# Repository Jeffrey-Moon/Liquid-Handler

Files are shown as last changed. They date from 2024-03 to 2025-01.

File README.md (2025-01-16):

# Construction of a Low-cost Liquid Handling Device with 3D Printing for Polymerase Chain Reaction V1

This repository contains the source code and instructions for constructing a low-cost automated liquid handling device designed specifically for performing Polymerase Chain Reaction (PCR) tasks. This device is ideal for underfunded laboratories looking for an affordable solution to automate repetitive pipetting tasks. For a clear and concise summary about the project, please read the [Construction of a Low-cost Liquid Handling Device with 3D Printing for Polymerase Chain Reaction.pdf](assets/Construction_of_a_Low-cost_Liquid_Handling_Device_with_3D_Printing_for_Polymerase_Chain_Reaction.pdf)

## Abstract

Although a field still in its infancy, robots, and automated devices have been adopted in an increasing number of laboratories to make the workflow more efficient. However, the high cost of liquid handling devices exacerbates disparities between laboratories. To address this issue, this research developed an accurate and low-cost liquid handler, designed for easy replication through open-source software and 3D designs distributed online. The device was rigorously tested, achieving a systematic error of 2.54% at 5 µL and a random error of 1.82%, yielding an overall accuracy of 97.46% and precision of 98.18%. Polymerase Chain Reaction (PCR) tests and gel electrophoresis analysis confirmed the machine’s capability to accurately perform PCR. With a material cost of approximately $206, this device offers a highly economical alternative to commercial liquid handlers, which typically range from $9,000 to $60,000. This innovation has the potential to significantly benefit underfunded laboratories, providing a cost-effective solution for repetitive PCR processes.

## Construction

The bill of materials and the details about the 3D print components are in the pdf [Liquid_Handler_Materials.pdf](assets/Liquid_Handler_Materials.pdf) (The bill of materials were last updated on Aug 19th, 2024 and the prices might have altered over time). Download the PDF to access the links used to buy each component. The required 3D print files are located in the stl folder.

## Running the Device

1. Clone the directory into the directory you desire by `git clone https://github.com/Jeffrey-Moon/Liquid-Handler.git`
1. Upload the Arduino code Liquid_Handler.ino after connecting the computer to the Arduino using the cable.
1. Plug in the device and turn the device on.
1. Download python if not already and download the required library by either running `pip install pyserial` or `pip install -r requirements.txt`.
1. Run the python code after creating your own sequence.

Example:
`python code/pyserial_control.py  --repetitions 1 2 3 --from_coords 0,0 1,1 2,2 --to_coords 3,3 4,4 5,5 --tube_types B T B`
This would execute a sequence of operations: First, attach a tip, then transfer from big tube (0,0) to small tube (3,3) once. Next, change the tip, then transfer from small tube (1,1) to small tube (4,4) twice. Finally, change the tip, then transfer from big tube (2,2) to small tube (5,5) three times.
--repetitions indicate the number of times the sequence will be executed. --from_coords is the coordinate that the device will pipette from and the --to_coords is the coordinate the device will pipette to. Lastly the --tube_types indicate the tube type for the pipetting. B indicates pipetting from the big tubes to the small tubes and T indicates pipetting from the small tubes to small tubes. The coordinate visualization for the tube racks are as seen below.

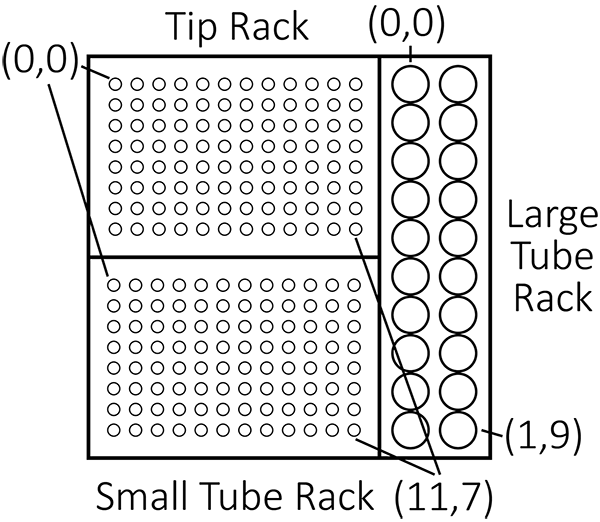
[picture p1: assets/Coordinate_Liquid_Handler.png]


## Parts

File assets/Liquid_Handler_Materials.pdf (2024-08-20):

Name | Price ($) | Amount | Total Price ($)
4 pcs 2020 V Type Aluminum Profile
300mm (https://www.amazon.com/dp/B0BZQCCP4P?ref=ppx_yo2ov_dt_b_product_details&th=1) | $ 15.99 | 3 | $ | 47.97
20 Sets Black 202 Series Aluminum
Profile Connector Set, 20 Pcs Comer
Bracker, 20Pcs T Nuts and Hex Screw
Bolt (https://www.amazon.com/dp/B0855V2JV3?ref=ppx_yo2ov_dt_b_product_details&th=1) | $ 19.97 | 1 | $ | 19.97
2 Pcs 5mm to 8mm Aluminum
Flexible Shaft Coupling D20 L25 (https://www.amazon.com/Zeberoxyz-Aluminium-Diameter20mm-Length25mm-Motor%EF%BC%885x8mm%EF%BC%89/dp/B08QV7SVH7?sp_csd=d2lkZ2V0TmFtZT1zcF9hdGY) | $ 11.99 | 1 | $ | 11.99
2 Pcs 8mm x 300mm Case Hardened
Chrome Plated Linear Motion Rod
Shaft Guide (https://www.amazon.com/dp/B07DPF612G?psc=1&ref=ppx_yo2ov_dt_b_product_details) | $ 9.99 | 2 | $ | 19.98

10 Pcs GT2 Pulley Wheel 20 Teeth
5mm Bore Aluminum Timing Belt Idler
Pulley for 3D Printer 6mm Width (https://www.amazon.com/3Dman-Pulley-Timing-Aluminum-Printer/dp/B085XLRXS1) | $ 8.99 | 1 | $ | 8.99
2 Pcs 8mm x 150mm Linear Motion
Rod Shaft Guide (https://www.amazon.com/dp/B08HYJTR54?psc=1&ref=ppx_yo2ov_dt_b_product_details) | $ 8.99 | 1 | $ | 8.99
GT2 Timing Belt 10 Meters Length
2mm Pitch 6mm Width Rubber Drive
Belt (https://www.amazon.com/dp/B097T3Y6WW?psc=1&ref=ppx_yo2ov_dt_b_product_details) | $ 9.99 | 1 | $ | 9.99
150mm Length T8 8mm Diameter
Lead Screw Rod with Copper Nut
Trapezoidal Thread for 3D Printer Z
Axis2pcs (https://www.amazon.com/dp/B07QV57SYP?psc=1&ref=ppx_yo2ov_dt_b_product_details) | $ 11.89 | 1 | $ | 11.89
1.5m 220V AC Cord (Only for 220V
countries) | $ 1.34 | 1 | $ | 1.34

Inc PS615143 3-Wire Appliance and
Power Tool Cord, 6 ft, 14 AWG,
15A/125V AC, 1875w , Black (https://www.amazon.com/dp/B07BQ8MRKR?psc=1&ref=ppx_yo2ov_dt_b_product_details) | $ 5.40 | 1 | $ | 5.40

3Pcs Nema 17 Stepper Motor
42BYGH 1.8 Degree 1.5A 42 Motor
(17HS4401S) 42N.cm (60oz.in) 4-
Lead with 1m Cable and Connector
for DIY CNC 3D Printer (Pack of 3) (https://www.amazon.com/dp/B07KW6B3ZX?psc=1&ref=ppx_yo2ov_dt_b_product_details) | $ 23.99 | 1 | $ | 23.99
6Pcs Round Rocker Switch AC 6A
125V 10A 250V SPST 3 Pins 2 Position
ON/Off Red and Green LED Light
Illuminated Round Boat Rocker
Switch Toggle (https://www.amazon.com/dp/B07QG1W93X?psc=1&ref=ppx_yo2ov_dt_b_product_details) | $ 7.99 | 1 | $ | 7.99

The prices were last updated on August 19th, 2024 and it may change over time

3D Printer CNC Shield V3 Engraver
Expansion Board with 4X A4988 Driver
Module and 4 x Radiator (https://www.amazon.com/dp/B07TT3C3HB?psc=1&ref=ppx_yo2ov_dt_b_product_details) | $ 10.99 | 1 | $ | 10.99
Arduino UNO R3 Board ATmega328P
w Cable (https://www.amazon.com/ATmega328P-Arduino-Compatible-Arduino-Voltage-Compatible/dp/B0D83J2TJJ) | $ 7.99 | 1 | $ | 7.99

DC 12V 10A 120W Power Supply
SMPS Adapter Transformer Switch AC
110V/220V to DC 12V 10A (https://www.amazon.com/dp/B078RTV9C4?psc=1&ref=ppx_yo2ov_dt_b_product_details) | $ 17.99 | 1 | $ | 17.99
Servo Tower Pro MG92B Digital Metal
Gear (https://www.aliexpress.us/item/3256805501735626.html?src=google&gatewayAdapt=glo2usa) | $ 8.53 | 1 | $ | 8.53
1kg PLA Filament (https://www.amazon.com/ELEGOO-Filament-Dimensional-Accuracy-Cardboard/dp/B0BM739JRF) | $ 13.99 | 2 | $ | 27.98

2020 V Type Aluminum Profile
300mm | $ (3.99) | 2 | $ | (7.98)
5mm to 8mm Aluminum Flexible
Shaft Coupling D20 L25 | $ (7.57) | 1 | $ | (7.57)

ST2 Pulley Wheel 20 Teeth 5mm
Bore Aluminum Timing Belt Idler
Pulley for 3D Printer 6mm Width | $ (1.24) | 8 | $ | (9.92)
Round Rocker Switch AC 6A 125V
10A 250V SPST 3 Pins 2 Position
ON/Off Red and Green LED Light
Illuminated Round Boat Rocker
Switch Toggle | $ (1.33) | 5 | $ | (6.65)
150mm Length T8 8mm Diameter
Lead Screw Rod with Copper Nut
Trapezoidal Thread for 3D Printer Z
Axis | $ (6.25) | 1 | $ | (6.25)
0.5 kg PLA filament | $ (7.62) | 1 | $ | (7.62)
SUM | $ | 205.99

EXCESS

Component Name Amount

Fillament
Weight (g)

Density
(%)

Total Weight
(g)
Working Area | 1 | 295.9 | 10 | 295.9
Pipette Tip Ejecctor | 1 | 0.5 | 10 | 0.5
Pipette Clamp | 1 | 88.7 | 75 | 88.7
Base Part | 4 | 119.4 | 50 | 477.6
Base Holder | 4 | 3.4 | 100 | 13.6
8mm Bore Linear Motion Guide
Helper | 4 | 2 | 100 | 8
8mm Bearing | 6 | 0.4 | 100 | 2.4

18mm Wide 6mm Belt 8mm
Bore Pulley Wheel Type 1 | 4 | 2 | 100 | 8

18mm Wide 6mm Belt 8mm
Bore Pulley Wheel Type 2 | 2 | 2.1 | 100 | 4.2
XY Axis Linear Guide Holder
Type 1 Left | 1 | 30.1 | 100 | 30.1
XY Axis Linear Guide Holder
Type 1 Right | 1 | 30.1 | 100 | 30.1
XY Axis Linear Guide Holder
Type 2 Left | 1 | 32.7 | 100 | 32.7
XY Axis Linear Guide Holder
Type 2 Right | 1 | 32.7 | 100 | 32.7
XY Axis Linear Motion Guide | 2 | 95.5 | 100 | 191
XY Axis Motor Holder Left | 1 | 75.7 | 100 | 75.7
XY Axis Motor Holder Right | 1 | 75.7 | 100 | 75.7
Z Axis Movement Bottom | 1 | 42.2 | 50 | 42.2
Z Axis Stepper Motor Body | 1 | 62.6 | 50 | 62.6
Z Axis Stepper Motor Top | 1 | 11.4 | 25 | 11.4
Large Tube Rack | 1 | 218 | 25 | 218
Servo Extension | 1 | 0.5 | 20 | 0.5
SUM | 1701.6

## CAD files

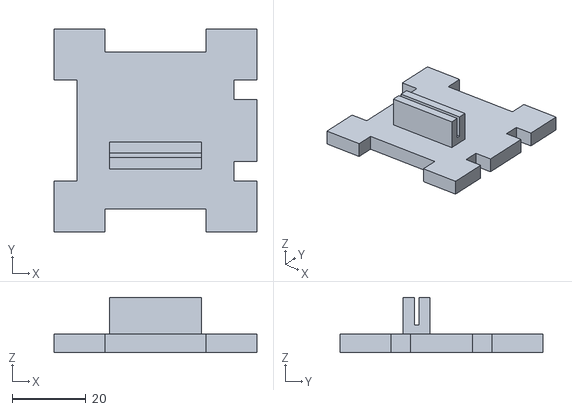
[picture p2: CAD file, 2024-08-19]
stl/Z Axis Stepper Motor Top.stl
55.0 x 55.0 x 15.0

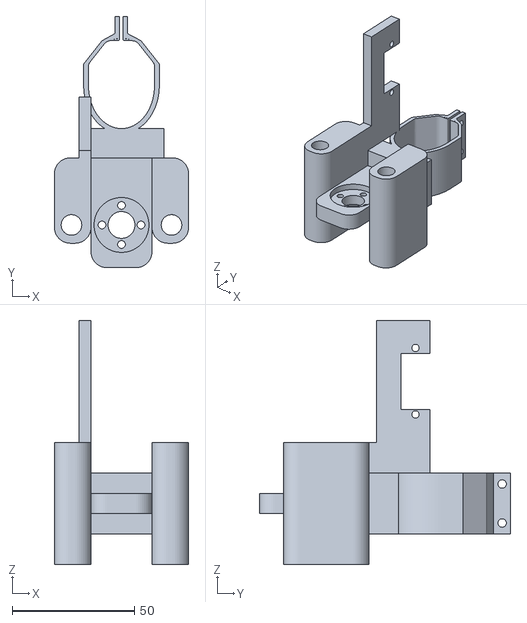
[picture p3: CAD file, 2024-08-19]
stl/Pipette Clamp.stl
55.0 x 103.0 x 100.0

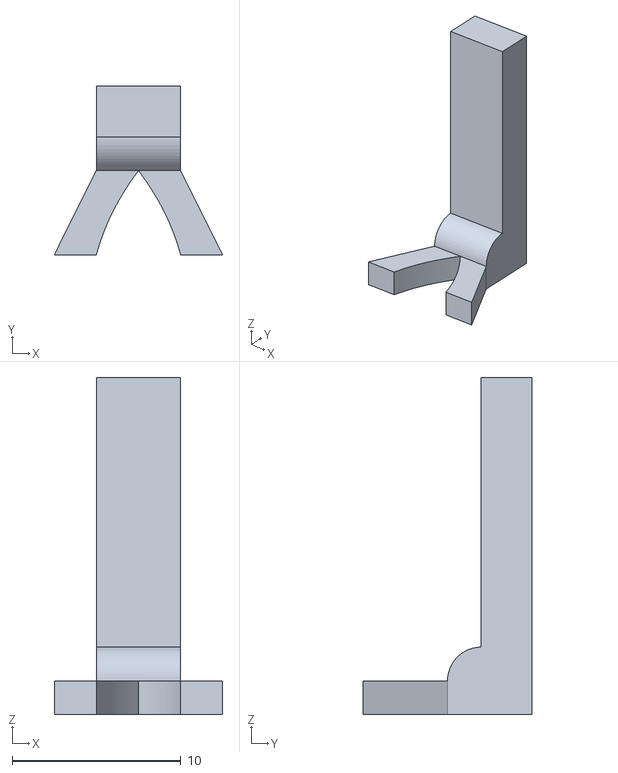
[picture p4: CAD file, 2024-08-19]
stl/Pipette Tip Ejector.stl
10.00 x 10.0 x 20.0

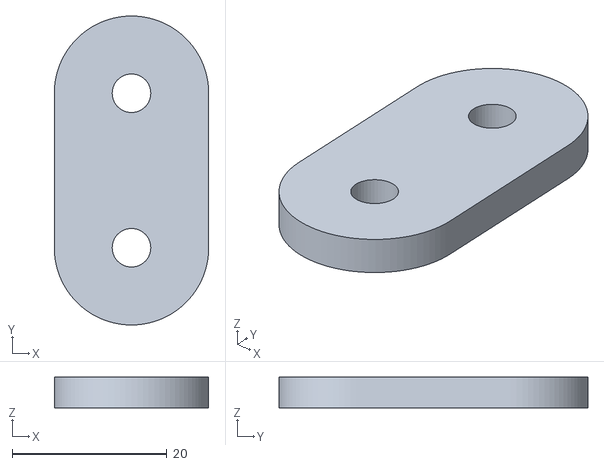
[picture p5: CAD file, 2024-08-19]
stl/Base Holder.stl
20.0 x 40.0 x 4.00

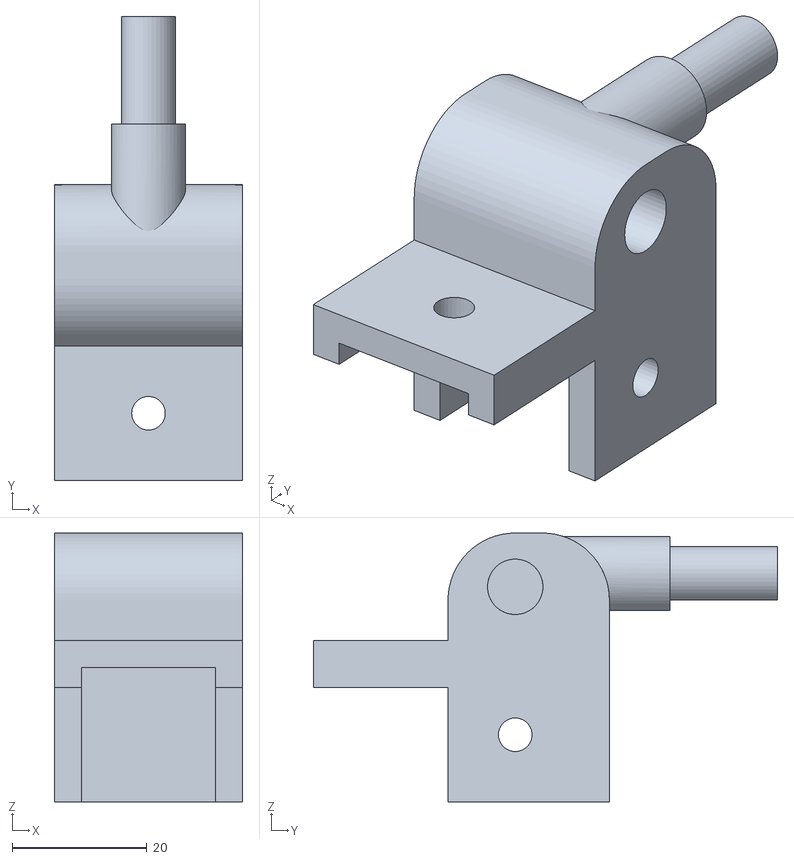
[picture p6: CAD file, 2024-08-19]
stl/XY Axis Linear Guide Holder Left.stl
28.0 x 69.0 x 40.0

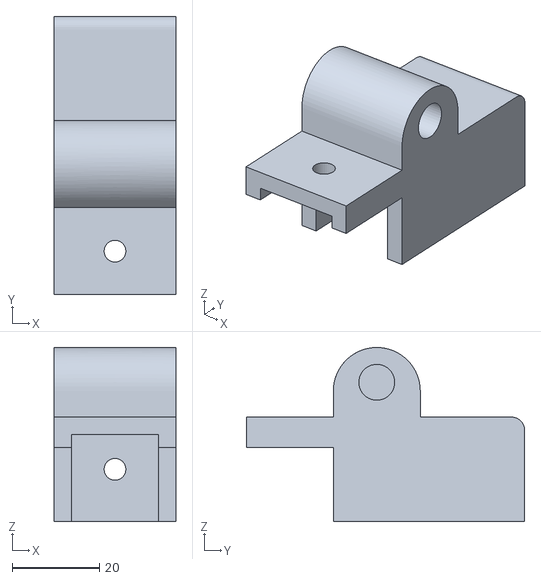
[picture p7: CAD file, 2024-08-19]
stl/XY Axis Linear Guide Holder 2 Right.stl
28.0 x 64.0 x 40.0

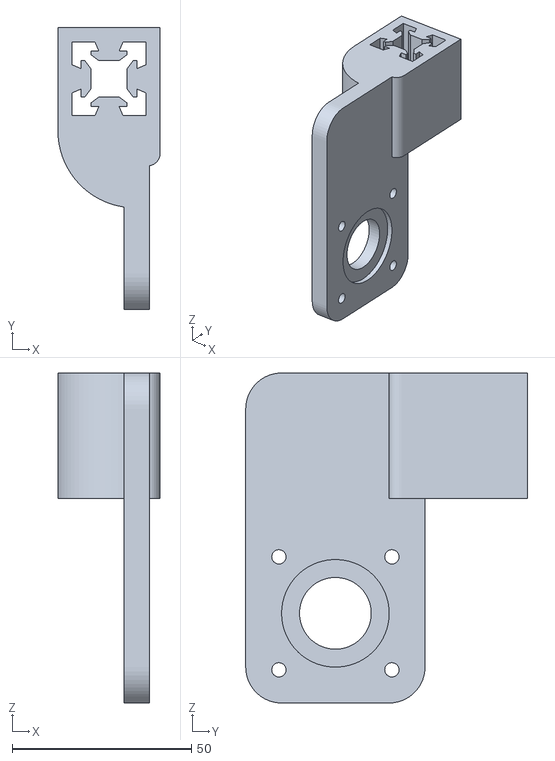
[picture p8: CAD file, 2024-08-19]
stl/XY Axis Motor Holder Left.stl
28.5 x 78.5 x 92.0

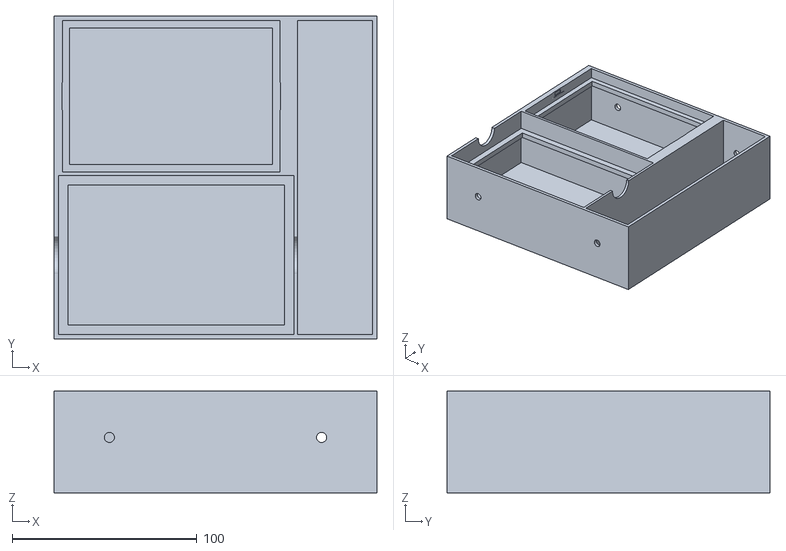
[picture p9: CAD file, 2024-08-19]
stl/Working Area.stl
175.0 x 175.0 x 55.0

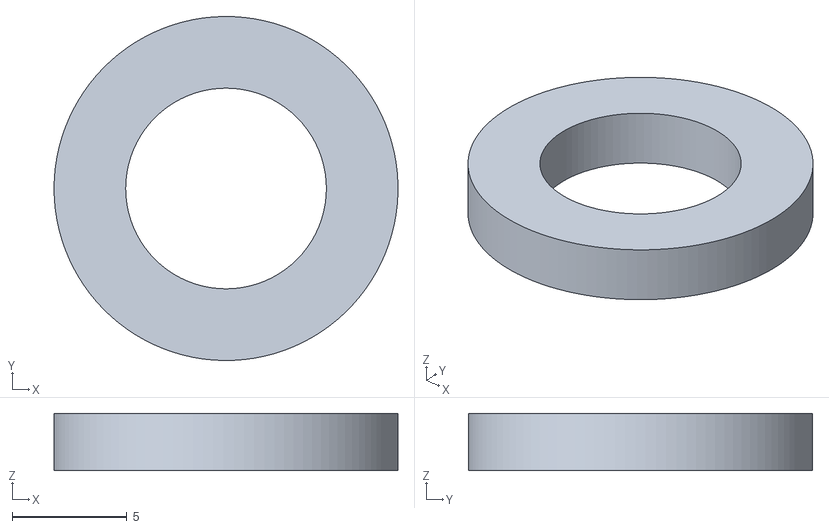
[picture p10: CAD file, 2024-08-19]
stl/8mm Bearing.stl
15.0 x 15.0 x 2.50

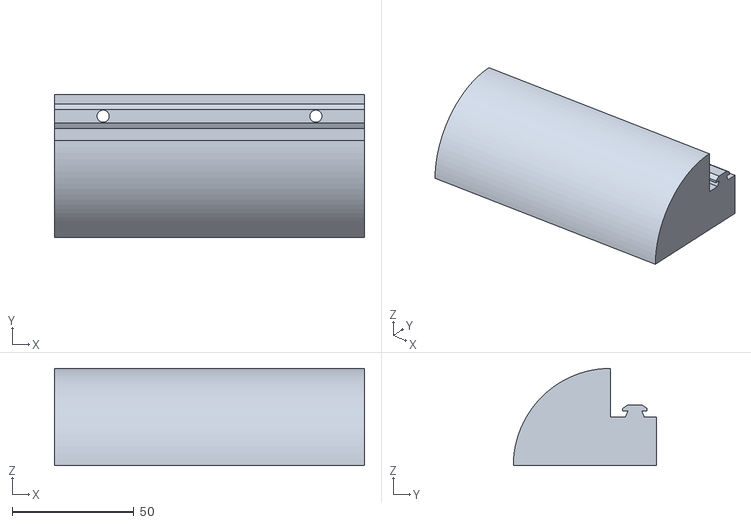
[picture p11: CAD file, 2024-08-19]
stl/Base Part.stl
127.5 x 59.0 x 40.0

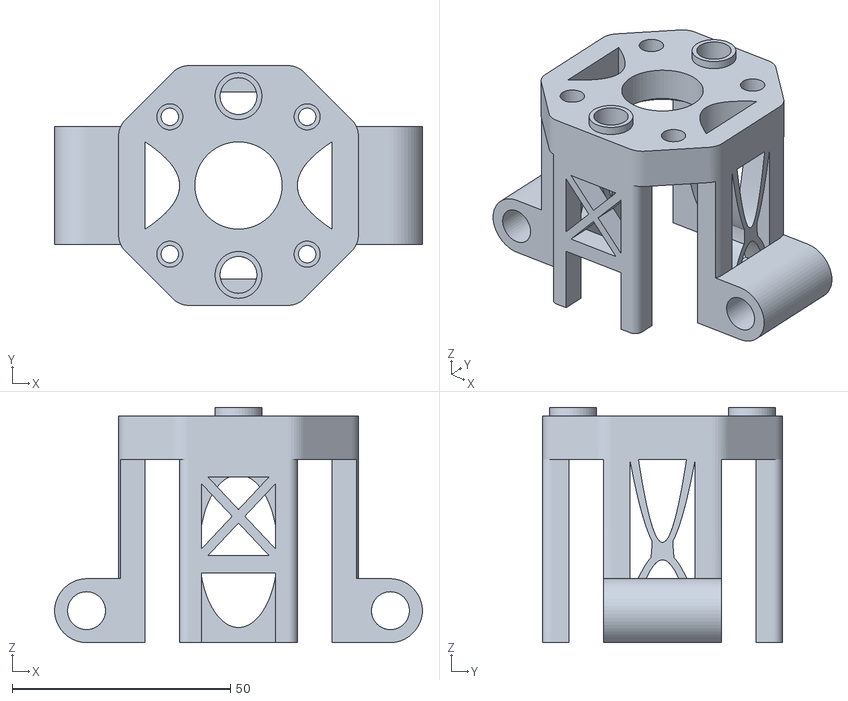
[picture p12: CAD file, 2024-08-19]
stl/Z Axis Stepper Motor Body.stl
84.4 x 55.0 x 54.0

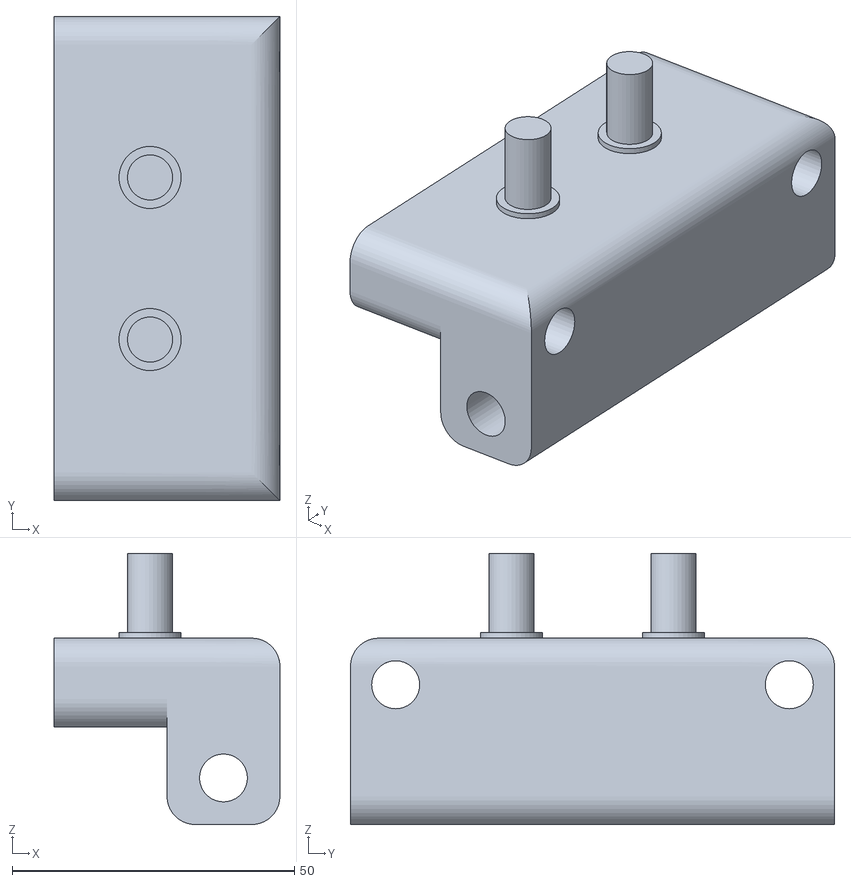
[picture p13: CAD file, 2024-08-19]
stl/XY Axis Linear Motion Guide.stl
40.0 x 85.7 x 48.0

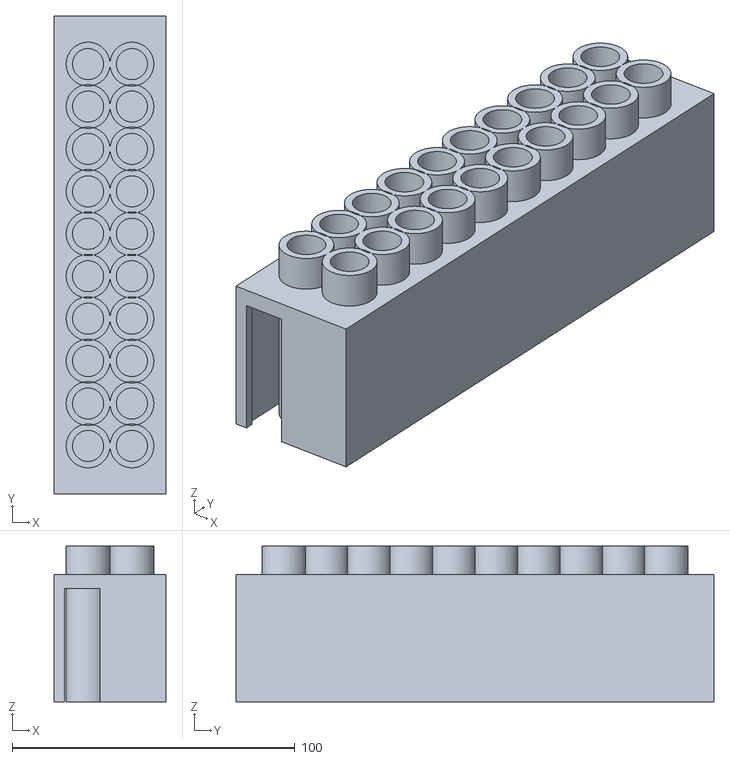
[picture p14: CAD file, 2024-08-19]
stl/Large Tube Rack.stl
39.5 x 169.0 x 55.0

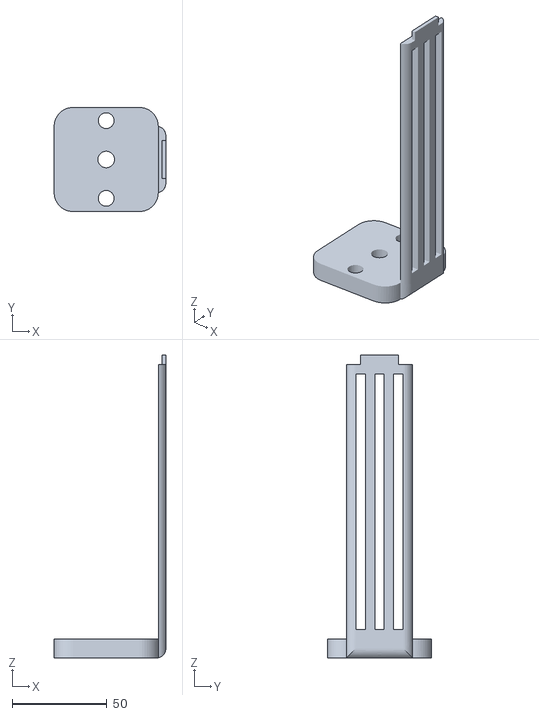
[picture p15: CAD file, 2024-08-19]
stl/Z Axis Movement Bottom.stl
59.0 x 55.0 x 160.0

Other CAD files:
stl/XY Axis Linear Guide Holder 2 Left.stl
stl/Servo Extension.stl
stl/XY Axis Linear Guide Holder Right.stl
stl/18mm wide 6mm belt 8mm bore Pulley Wheel Type 2.stl
stl/18mm wide 6mm belt 8mm bore Pulley Wheel.stl
stl/8mm Bearing Linear Motion Guide Helper.stl
stl/XY Axis Motor Holder Right.stl

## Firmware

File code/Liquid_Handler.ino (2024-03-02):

// Import Libraries
#include <Servo.h>

// Declaring Servo
Servo myservo;

// Class of coordinate
class Coordinate {
public:
  int X;
  int Y;
  Coordinate()
  {
    Serial.println("Coordinate initialized");
    X = 0;
    Y = 0;
  }
  Coordinate(int x, int y)
  {
    X = x;
    Y = y;
  }
  void PrintCoor() 
  {
    Serial.println("X Coordinate: ");
    Serial.println(X);
    Serial.println("Y Coordinate: ");
    Serial.println(Y);
  }
};

// Boolean values that acts as indicators
bool runComplete = false; // boolean indicating if the loop completed once

// Boolean two dimensional array of the tip rack to indicate if the tip rack slots are empty or not
bool tipRack[8][12] = {1};

// The designated pin numbers
const int enPin = 8;
const int stepXPin = 2; //X.STEP
const int dirXPin = 5; // X.DIR
const int stepYPin = 3; //Y.STEP
const int dirYPin = 6; // Y.DIR
const int stepZPin = 4; //Z.STEP
const int dirZPin = 7; // Z.DIR
const int servoPin = 11; // Servo

// Stepper motor variables
const int stepsPerRev = 200;
int pulseWidthMicros = 100;  // microseconds
int millisBtwnStepsXY = 615;
int millisBtwnStepsZ = 1000;

// Gaps inbetween the tip rack slots and tube rack slots
const int tipGap_X = 45.56;
const int tipGap_Y = 45.6;
const int tubeGap_X = 46;
const int tubeGap_Y = 46;
const int bigTubeGap_X = 75;
const int bigTubeGap_Y = 75.33;

// Number of tips used
int tipCnt = 0;

// Declaration of coordinates of specific places and the current position
Coordinate *curPos = new Coordinate();
Coordinate *firstTipPos = new Coordinate(194, 45); 
Coordinate *firstTubePos = new Coordinate(195.5, 477);
Coordinate *firstBigTubePos = new Coordinate(845, 89);
Coordinate *tipEjection = new Coordinate(1015, 240);
Coordinate *origin = new Coordinate(0, 0);

// setup function for enabling motors and the CNC shield
void setup() {
  Serial.begin(9600);
  pinMode(enPin, OUTPUT);
  digitalWrite(enPin, LOW);
  Serial.println(F("CNC Shield Enabled"));

  pinMode(stepXPin, OUTPUT);
  pinMode(dirXPin, OUTPUT);
  pinMode(stepYPin, OUTPUT);
  pinMode(dirYPin, OUTPUT);
  pinMode(stepZPin, OUTPUT);
  pinMode(dirZPin, OUTPUT);
  Serial.println(F("Stepper Motor Initialized"));

  myservo.attach(servoPin);
  Serial.println(F("Servo Motor Initialized"));

  Serial.println(F("Initial Position: "));
  curPos->PrintCoor();
  return;
}
// function for pressing the pipette with the servo (servo val: 15)
void pressPipette() {
  myservo.write(73.45);
  delay(1000);
}
// 
void emptyPipette() {
  myservo.write(25);
  delay(1000);
}
// function for releasing the pipette with the servo (servo val: 165)
void releasePipette(bool pressto=0) {
  if (pressto) {
    for (int i = 74.5; i < 166; i++){
      myservo.write(i);
      delay(4);
    }
  }
  else {
    myservo.write(165);
  }
  delay(1000);
}
// function for raising the pipette with the Z Axis stepper motor
void raisePipette(bool from=0) {
  Serial.println(F("Positive Z Movement"));
  digitalWrite(dirZPin, LOW); // Enables the motor to move in a particular direction
  // Makes 1000 pulses for making one full cycle rotation
  int steps;
  if (curPos->X < 840 && curPos->X > 50)
  {
    if (curPos->Y <= 475)
    {
      Serial.println(F("Tip Rack Z Movement"));
      steps = stepsPerRev * 7.34;
    }
    else
    {
      Serial.println(F("Tube Race Z Movement"));
      if (from)
      {
        steps = stepsPerRev * 5.205;
      }
      else
      {
        // steps = stepsPerRev * 5.075;
        steps = stepsPerRev * 4.9;
      }
    }
  }
  else if (curPos->X >= 840)
  {
    if (curPos->X >= 1000)
    {
      Serial.println(F("Tip Ejection Z Movement"));
      steps = stepsPerRev * 7.2;
    }
    else 
    {
      Serial.println(F("Big Tube Z Movement"));
      steps = stepsPerRev * 6.81;
      // 6.9 
    }
  }
  else
  {
    Serial.println(F("ERROR: Coordinate Not Found"));
    steps = stepsPerRev * 1;
  }
  for (int i = 0; i < steps; i++) {
    digitalWrite(stepZPin, HIGH);
    delayMicroseconds(pulseWidthMicros);
    digitalWrite(stepZPin, LOW);
    delayMicroseconds(millisBtwnStepsZ);
  }
  delay(1000); // One second delay
}
// function for lowering the pipette with the Z Axis stepper motor
void lowerPipette(bool from=0) {
  Serial.println(F("Negative Z Movement"));
  digitalWrite(dirZPin, HIGH); // Enables the motor to move in a particular direction
  // Makes 1000 pulses for making one full cycle rotation       
  int steps;
   if (curPos->X < 840 && curPos->X > 50)
  {
    if (curPos->Y <= 475)
    {
      Serial.println(F("Tip Rack Z Movement"));
      steps = stepsPerRev * 7.34;
    }
    else
    {
      Serial.println(F("Tube Race Z Movement"));
      if (from)
      {
        steps = stepsPerRev * 5.205;
      }
      else
      {
        // steps = stepsPerRev * 5.075;
        steps = stepsPerRev * 4.9;
      }
    }
  }
  else if (curPos->X >= 840)
  {
    if (curPos->X >= 1000)
    {
      Serial.println(F("Tip Ejection Z Movement"));
      steps = stepsPerRev * 7.2;
    }
    else 
    {
      Serial.println(F("Big Tube Z Movement"));
      steps = stepsPerRev * 6.813;
      // 6.9
    }
  }
  else
  {
    Serial.println(F("ERROR: Coordinate Not Found"));
    steps = stepsPerRev * 1;
  }

  for (int i = 0; i < steps; i++) {
    digitalWrite(stepZPin, HIGH);
    delayMicroseconds(pulseWidthMicros);
    digitalWrite(stepZPin, LOW);
    delayMicroseconds(millisBtwnStepsZ);
  }
  delay(1000); // One second delay
}
// function for moving the body in the X coordinate by spinning the XY Axis stepper motors in oppostie directions
void moveX(int stepNum) {
  if (stepNum < 0) {
    Serial.println(F("Negative X Movement"));
    digitalWrite(dirXPin, HIGH); // Enables the motor to move in a particular direction
    digitalWrite(dirYPin, HIGH); // Enables the motor to move in a particular direction
    // Makes 200 pulses for making one full cycle rotation
    for (int i = 0; i < -stepNum; i++, curPos->X--) {
      digitalWrite(stepXPin, HIGH);
      delayMicroseconds(pulseWidthMicros);
      digitalWrite(stepXPin, LOW);
      delayMicroseconds(millisBtwnStepsXY);
      digitalWrite(stepYPin, HIGH);
      delayMicroseconds(pulseWidthMicros);
      digitalWrite(stepYPin, LOW);
      delayMicroseconds(millisBtwnStepsXY);
    }
    delay(1000); // One second delay
  }
  else {
    Serial.println(F("Positive X Movement"));
    digitalWrite(dirXPin, LOW); //Changes the rotations direction
    digitalWrite(dirYPin, LOW); //Changes the rotations direction
    // Makes 200 pulses for making two full cycle rotation
    for (int i = 0; i < stepNum; i++, curPos->X++) {
      digitalWrite(stepXPin, HIGH);
      delayMicroseconds(pulseWidthMicros);
      digitalWrite(stepXPin, LOW);
      delayMicroseconds(millisBtwnStepsXY);
      digitalWrite(stepYPin, HIGH);
      delayMicroseconds(pulseWidthMicros);
      digitalWrite(stepYPin, LOW);
      delayMicroseconds(millisBtwnStepsXY);
    }
    delay(1000);
  }
  return;
}
// function for moving the body in the Y coordinate by spinning the XY Axis stepper motors in the same direction
void moveY(int stepNum) {
  if (stepNum < 0) 
  {
    Serial.println(F("Negative Y Movement"));
    digitalWrite(dirXPin, HIGH); // Enables the motor to move in a particular direction
    digitalWrite(dirYPin, LOW); // Enables the motor to move in a particular direction
    // Makes 200 pulses for making one full cycle rotation
    for (int i = 0; i < -stepNum; i++, curPos->Y--) {
      digitalWrite(stepXPin, HIGH);
      delayMicroseconds(pulseWidthMicros);
      digitalWrite(stepXPin, LOW);
      delayMicroseconds(millisBtwnStepsXY);
      digitalWrite(stepYPin, HIGH);
      delayMicroseconds(pulseWidthMicros);
      digitalWrite(stepYPin, LOW);
      delayMicroseconds(millisBtwnStepsXY);
    }
    delay(1000); // One second delay
  }
  else
  {
    Serial.println(F("Positive Y Movement"));
    digitalWrite(dirXPin, LOW); //Changes the rotations direction
    digitalWrite(dirYPin, HIGH); //Changes the rotations direction
    // Makes 200 pulses for making two full cycle rotation
    for (int i = 0; i < stepNum; i++, curPos->Y++) {
      digitalWrite(stepXPin, HIGH);
      delayMicroseconds(pulseWidthMicros);
      digitalWrite(stepXPin, LOW);
      delayMicroseconds(millisBtwnStepsXY);
      digitalWrite(stepYPin, HIGH);
      delayMicroseconds(pulseWidthMicros);
      digitalWrite(stepYPin, LOW);
      delayMicroseconds(millisBtwnStepsXY);
    }
    delay(1000);
  }
  return;
}
// moving to a given coordinate from another coordinate by moving the X and then moving the Y (the coordinate a will usually be curPos)
void goTo(Coordinate *a, Coordinate *b) {
  int X_movement = b->X - a->X;
  int Y_movement = b->Y - a->Y;
  moveX(X_movement);
  moveY(Y_movement);
  return;
}
// Go to the origin and reset the servo motor
void reset() {
  goTo(curPos, origin);
  releasePipette();
  return;
}
void B2TPipette(int X, int Y, int x, int y) {
  goTo(curPos, new Coordinate(firstBigTubePos->X + X * bigTubeGap_X, firstBigTubePos->Y + Y * bigTubeGap_Y));
  pressPipette();
  lowerPipette();
  delay(500);
  releasePipette(1);
  delay(300);
  raisePipette();
  goTo(curPos, new Coordinate(firstTubePos->X + x * tubeGap_X, firstTubePos->Y + y * tubeGap_Y));
  lowerPipette();
  emptyPipette();
  raisePipette();
  releasePipette();
}
// Pipette the liquid from (x1, y1) to (x2, y2)
void T2TPipette(int x1, int y1, int x2, int y2) {
  goTo(curPos, new Coordinate(firstTubePos->X + x1 * tubeGap_X, firstTubePos->Y + y1 * tubeGap_Y));
  pressPipette();
  lowerPipette(1);
  delay(500);
  releasePipette(1);
  delay(300);
  raisePipette(1);
  goTo(curPos, new Coordinate(firstTubePos->X + x2 * tubeGap_X, firstTubePos->Y + y2 * tubeGap_Y));
  lowerPipette();
  emptyPipette();
  raisePipette();
  releasePipette();
  return;
}
// Eject the current tip and attach the next tip on the tip rack
void Tip() {
  if (tipCnt != 0)
  {
    goTo(curPos, new Coordinate(tipEjection->X, 0));
    lowerPipette();
    goTo(curPos, new Coordinate(tipEjection->X, tipEjection->Y));
    raisePipette();
  }
  Coordinate *nextTip = new Coordinate(firstTipPos->X + (tipCnt%12) * tipGap_X, firstTipPos->Y + (tipCnt/12) * tipGap_Y);
  nextTip->PrintCoor();
  goTo(curPos, nextTip);
  lowerPipette();
  raisePipette();
  tipCnt++;
  return;
}
// Test for the first coordiante of the tip rack
void TestTip(int a) {
  Coordinate *nextTip = new Coordinate(firstTipPos->X + (a%12) * tipGap_X, firstTipPos->Y + (a/12) * tipGap_Y);
  goTo(curPos, nextTip);
  lowerPipette();
  raisePipette();
}

void loop() {
  if (!runComplete)
  {
    // ====================== Code Begins Here ======================
    delay(1000);
    releasePipette();
    
    //int array[5] = {5, 1, 0, 2, 0};
    //int array[5] = {1, 0, 0, 0, 1};
    //example array of moves
    int array[5] = {0, 0, 2, 0, 1};
    for (int i = 0; i <= 4; i++)
    {
      if (array[i] != 0){
        Tip();
      }
      for (int j = 0; j < array[i]; j++)
      {
        Serial.println(F("Loop"));
        B2TPipette(0, i, 0, 0);
      }
    }
    
    //TestTip(95);
    // while(true){
    //   B2TPipette(0, 0, 0, 0);
    // }

    reset();
    // ======================= Code Ends Here =======================
    runComplete = true;
  }
}
  

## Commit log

2024-08-19 Initial Release
    [18mm wide 6mm belt 8mm bore Pulley Wheel Type 2.stl, 18mm wide 6mm belt 8mm bore Pulley Wheel.stl, 8mm Bearing Linear Motion Guide Helper.stl, 8mm Bearing.stl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]
2024-08-20 Updated minor naming errors
    [Large Tube Rack.stl, Servo Extension.stl]
2024-08-21 Updated to print time for sequences
